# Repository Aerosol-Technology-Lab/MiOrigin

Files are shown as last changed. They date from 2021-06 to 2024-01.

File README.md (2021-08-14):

# MiOrigin
This device is a controller for a bioaerosol collector used by the [Aerosol Technology Lab](https://aerosoltechnologylab.tamu.edu/) of the Biological and Agricultural Engineering Department at Texas A&M University. The MiOrigin controller mimics the MiClone software, which requires a PC connection to use.
 
 ### Features
 - ESP32-WROOM-32E (16MB) MCU
 - 3.5" 480x320 touch-enabled LCD
 - Rechargeable 1000mAh LiPo battery via USB-C connector
 - Built-in male RS-232 port (MAX3232 RS-232 Line Driver) 
 - Over-the-air (OTA) update via BLE

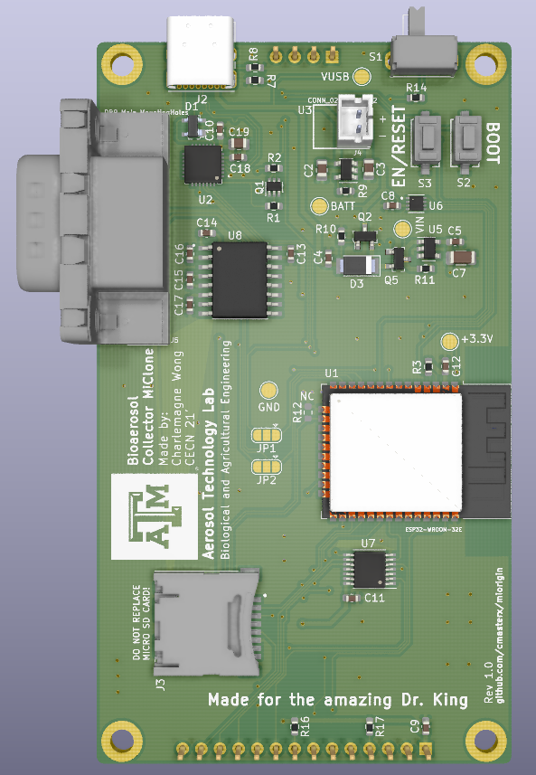
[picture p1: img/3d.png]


## Branches

## USB Drivers for Windows, Linux, macOS
Install CP210x driver if device cannot be detected by computer if connecting to the controller via USB

- Download [CP210x Drivers](https://www.silabs.com/developers/usb-to-uart-bridge-vcp-drivers)

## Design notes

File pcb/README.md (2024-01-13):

# MiOrigin Controller PCB
PCB Schematic and Layour for MiOrigin Controller designed on KiCad

## Revisions
### Rev 1.1 
#### Updates since past revision (Rev 1.0)
1. Moved protection USB diodes to the front of the board
1. Replaced wrong footprint with correct size for the Tri-State Buffer (see Rev 1.0-Known Issue #2)

#### Known Issues
1. RS-232 TX and RX line are switched between the MAX-3232 IC and the D-Sub port. Continuing issue from previous revision (see Rev 1.0-Known Issue #1)

### Rev 1.0
#### Known Issues
1. RS-232 TX and RX line are switched between the MAX-3232 IC and the D-Sub port
1. Footprint for Tri-State Buffer is smaller than actual IC. Careful soldering is required

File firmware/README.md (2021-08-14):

# MiOrigin Controller Firmware
Firmware for MiOrigin Controller

## Setup
1. Install PlatformIO for VS Code
1. Copy boards information from [./boards](boards/) to .platformio boards path

## Build and Flashing Firmware

### Intro
The MiOrigin controller requires two firmwares - a "factory" firmware and an "ota" firmware.

The ota firmware is the actual running firmware during normal operation. This firmware contains the functions that controls the bioaerosol collector. The factory firmware is a special bootloader firmware used to update the ota firmware.

In normal operation, the ota firmware will always boot over the factory firmware. If an update is available over BLE or a new ota firmware is present in the root directory of the MicroSD card, the ota firmware reboots to the factory firmware. The factory firmware flashes the new ota firmware, delete the old copy of the ota firmware in the MicroSD card at `/firmware` (if exists), then places a copy of the new firmware into that directory. If successful, the controller reboots to the newly flashed ota firmware.

### Note

### Flash Factory Firmware
1. Under PlatformIO Extension on the left sidebar, open Project Tasks
1. Select `Build` under `factory` firmware
1. Flash `factory` firwmare with either options:
    1. Connect laptop to control board with a USB-C cable
    1. Select `Upload` to flash directly to firmware
        - Choose this option if this is the first time flashing the board. This will update the correct partition table to the flash
    - add factory firmware with filename `factory.bin` to the root directory of the MicroSD card
        - Note: This is possible only if ota firmware has been previously flashed to the board. This is not possible with a board with no previous programming

### Flash OTA Firmware
1. Under PlatformIO Extension on the left sidebar, open Project Tasks
1. Build `ota` firwmare
1. Flash `factory` firmware with either options 
    - add ota firmware with filename `firmware.bin` to the root directory of the MicroSD card
    1. Connect laptop to control board with a USB-C cable
    1. flash with esptool `$ python3 esptool.py COM_PORT write_flash 0x110000 /path/to/firmware.bin`
        - NOTE: Address used for firmware in flash is `0x110000`. Verify beforing flashing by checking Offset address of `ota_0` in the [partition table](partition_table.csv)

### Pre-compiled firmwares
Pre-compiled firmwares are available at `todo: do this`

## Pipeline
- [x] TFT SPI LCD drivers
- [x] Post scripts that generates pre-compiled firmware/binaries
- [x] WiFi with keep awake
- [x] WiFi WPA
- [ ] WiFi WPA2 Enterprise
- [ ] BLE device settings
- [ ] Update over WiFi

## Known Issues
- Touch screen not working

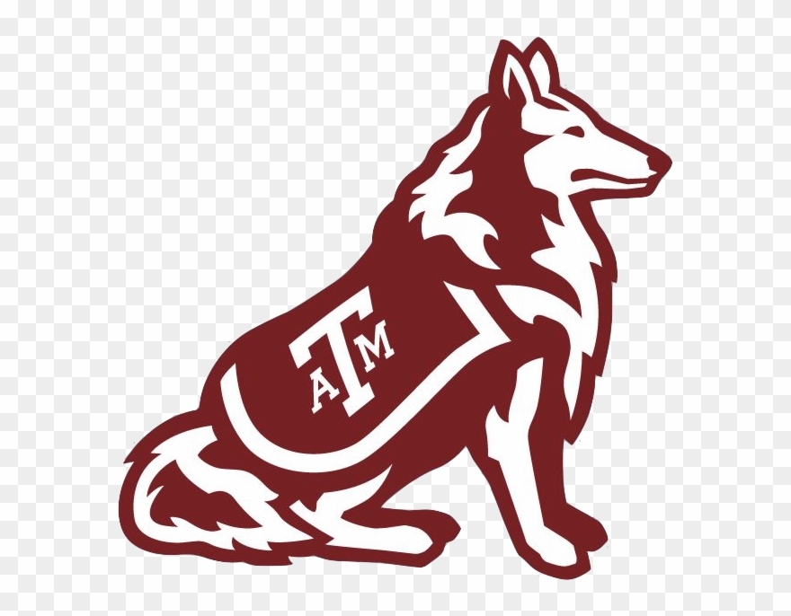
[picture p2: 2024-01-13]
pcb-power-share/power-share/assets/rev.jpg

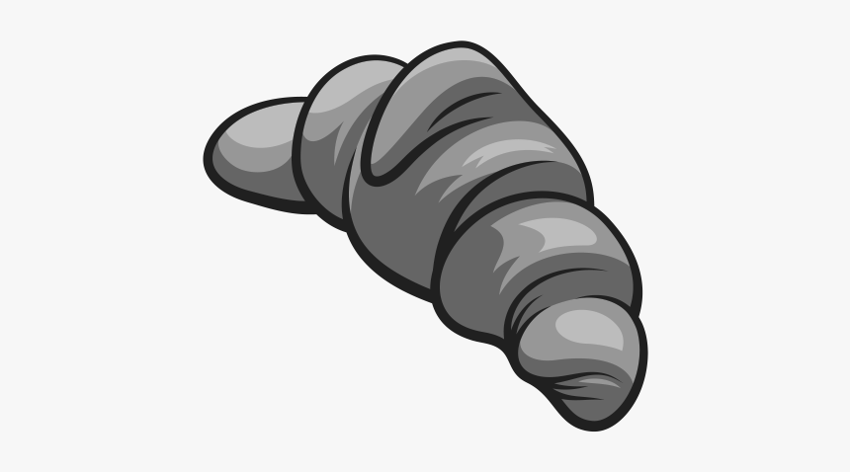
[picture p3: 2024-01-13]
pcb-power-share/power-share/assets/croissant.bmp

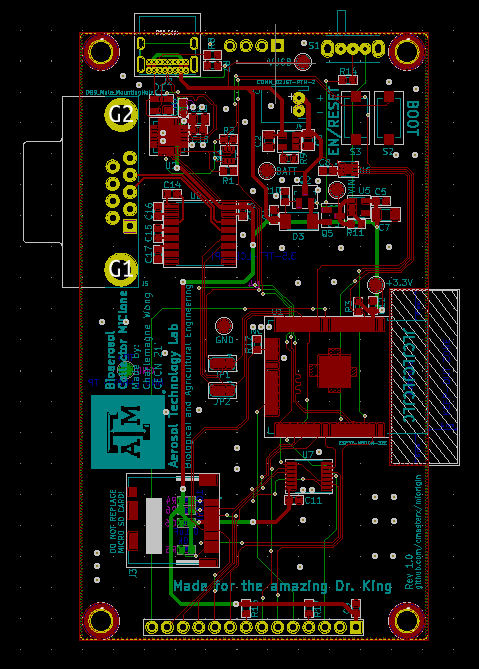
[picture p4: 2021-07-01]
img/outline.png

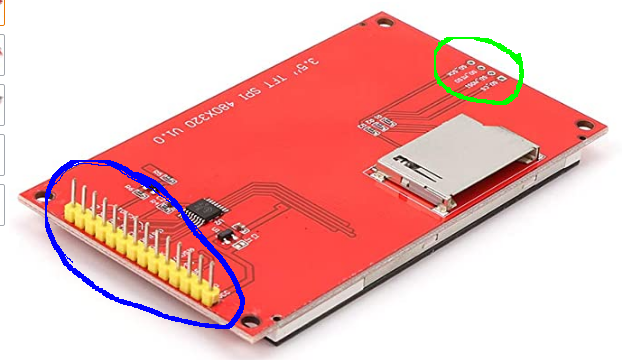
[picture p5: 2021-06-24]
img/display.png

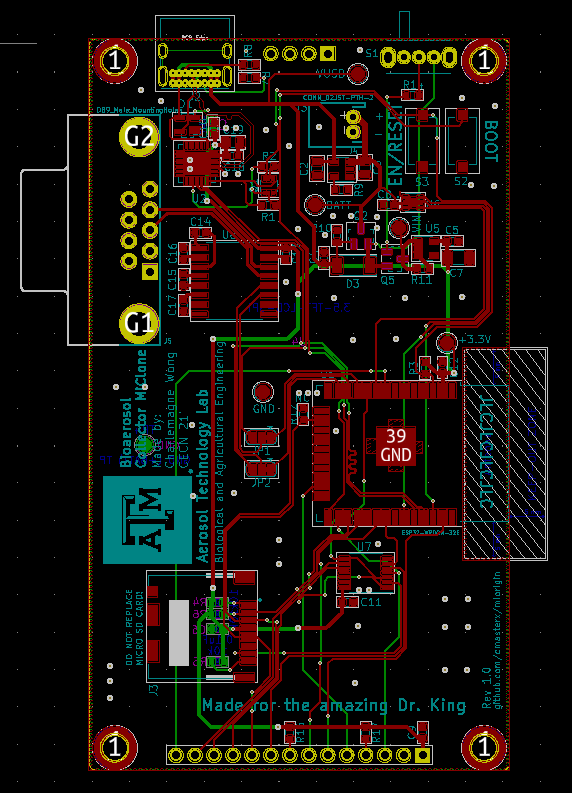
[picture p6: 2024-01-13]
img/outline2.png

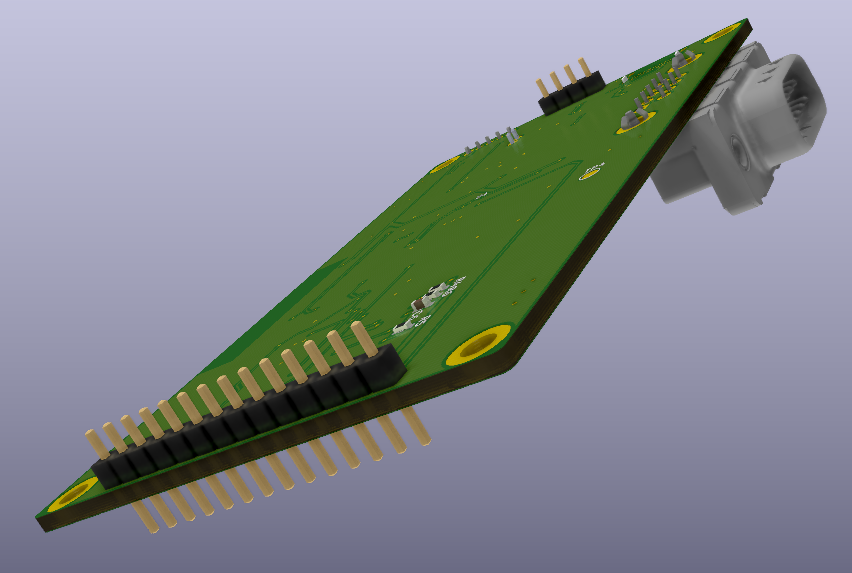
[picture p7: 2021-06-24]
img/Screenshot from 2021-06-24 16-22-36.png

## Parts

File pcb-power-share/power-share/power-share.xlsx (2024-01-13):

Prj: | power-share.xml |  |  |  | Board Qty: | 100
Co.: |  |  |  |  | Unit Cost: | $7.39
Prj date: | Fri 22 Oct 2021 12:46:14 AM CDT |  |  |  | Total Cost: | $738.93 |  |  |  |  | $374.99 | 6 of 15 parts found |  |  |  |  | $839.45 | 8 of 15 parts found |  |  |  |  | $532.62 | 6 of 15 parts found |  |  |  |  | $2.94 | 1 of 15 parts found |  |  |  |  | $483.30 | 7 of 15 parts found |  |  |  |  | $505.60 | 6 of 15 parts found |  |  |  |  | $542.02 | 6 of 15 parts found |  |  |  |  | $41.28 | 1 of 15 parts found
$ date: | 2021-10-22 00:49:18
Global Part Info |  |  |  |  |  |  | Arrow |  |  |  |  |  | Digi-Key |  |  |  |  |  | Farnell |  |  |  |  |  | LCSC |  |  |  |  |  | Mouser |  |  |  |  |  | Newark |  |  |  |  |  | RS Components |  |  |  |  |  | TME
Refs | Value | Footprint | Manf# | Qty | Unit$ | Ext$ | Avail | Purch | Unit$ | MOQ | Ext$ | Cat# | Avail | Purch | Unit$ | MOQ | Ext$ | Cat# | Avail | Purch | Unit$ | MOQ | Ext$ | Cat# | Avail | Purch | Unit$ | MOQ | Ext$ | Cat# | Avail | Purch | Unit$ | MOQ | Ext$ | Cat# | Avail | Purch | Unit$ | MOQ | Ext$ | Cat# | Avail | Purch | Unit$ | MOQ | Ext$ | Cat# | Avail | Purch | Unit$ | MOQ | Ext$ | Cat#
C1 | 22uF | CP_Elec_8x6.5 | 865080643008 | 100 | $0.191 | $19.10 |  |  |  |  |  |  | 8623 |  | $0.198 | 1 | $19.80 | 732-8453-1-ND (https://octopart.com/click/track?ai=8078&sig=08143f3&sid=459&ppid=53914617&vpid=240502649&ct=offers) | NonStk |  | $0.373 | 1 | $37.28 | 2466335 (https://octopart.com/click/track?c=1&ai=8078&sig=09a3c48&sid=819&ppid=53914617&vpid=209558840&ct=offers) |  |  |  |  |  |  | NonStk |  | $0.191 | 1 | $19.10 | 710865080643008 (https://octopart.com/click/track?c=1&ai=8078&sig=0967f77&sid=2401&ppid=53914617&vpid=416614858&ct=offers) | NonStk |  | $0.253 | 1 | $25.30 | 40Y4050 (https://octopart.com/click/track?c=1&ai=8078&sig=09bb828&sid=2402&ppid=53914617&vpid=184773775&ct=offers) | 225 |  | $0.287 | 25 | $28.72 | 8391874 (https://octopart.com/click/track?ai=8078&sig=06ba437&sid=10022&ppid=53914617&vpid=199199319&ct=offers)
C2 | 6.8uF | C_1812_4532Metric | C4532X7R1H685K250KB | 100 | $0.768 | $76.85 | NonStk |  | $1.207 | 1 | $120.71 | C4532X7R1H685K250KB (https://octopart.com/click/track?c=1&ai=8078&sig=0d2d5fb&sid=1106&ppid=25947926&vpid=486097657&ct=offers) | 19867 |  | $0.768 | 1 | $76.85 | 445-3919-1-ND (https://octopart.com/click/track?ai=8078&sig=02ae9c6&sid=459&ppid=25947926&vpid=63975951&ct=offers) | 59500 |  | $0.850 | 1 | $85.04 | 1843170 (https://octopart.com/click/track?ai=8078&sig=0c89169&sid=819&ppid=25947926&vpid=139697936&ct=offers) |  |  |  |  |  |  | 8166 |  | $0.769 | 1 | $76.90 | 810C4532X7R1H685K (https://octopart.com/click/track?ai=8078&sig=00ac762&sid=2401&ppid=25947926&vpid=66164902&ct=offers) | 59000 |  | $1.060 | 1 | $106.00 | 13T1119 (https://octopart.com/click/track?ai=8078&sig=08b8ed0&sid=2402&ppid=25947926&vpid=260822761&ct=offers) | 16131 |  | $1.483 | 5 | $148.28 | 7416825 (https://octopart.com/click/track?ai=8078&sig=0acb252&sid=10022&ppid=25947926&vpid=199138110&ct=offers)
C3 | 10nF | C_0402_1005Metric_Pad0.74x0.62mm_HandSolder | GCM155R71H103KA55D | 100 | $0.013 | $1.29 | 2269 |  |  | 10000 |  | GCM155R71H103KA55D (https://octopart.com/click/track?ai=8078&sig=0baf4ca&sid=1106&ppid=9105516&vpid=473329314&ct=offers) | 25744106 |  | $0.013 | 1 | $1.29 | 490-4762-1-ND (https://octopart.com/click/track?ai=8078&sig=05479c9&sid=459&ppid=9105516&vpid=34232110&ct=offers) | 8250000 |  | $0.021 | 10 | $2.06 | 2470416RL (https://octopart.com/click/track?ai=8078&sig=0119398&sid=819&ppid=9105516&vpid=220678719&ct=offers) | 97850 |  | $0.029 | 50 | $2.94 | C91601 (https://octopart.com/click/track?ai=8078&sig=0ec5f8f&sid=27971&ppid=9105516&vpid=445986708&ct=offers) | 7456658 |  | $0.018 | 1 | $1.80 | 81GCM155R71H103KA5D (https://octopart.com/click/track?ai=8078&sig=048b060&sid=2401&ppid=9105516&vpid=37821366&ct=offers) | 8250000 |  | $0.022 | 1 | $2.20 | 45Y5159 (https://octopart.com/click/track?ai=8078&sig=031832d&sid=2402&ppid=9105516&vpid=231884079&ct=offers) | 607000 |  |  | 200 |  | 7234954 (https://octopart.com/click/track?ai=8078&sig=0a8e140&sid=10022&ppid=9105516&vpid=199071532&ct=offers)
C4 | 120uF | C_Elec_4x5.8 | https://b2b-api.panasonic.eu/file_stream/pids/fileversion/9127 | 100
C5,C7 | 10uF | C_0805_2012Metric | CL21B106KOQNNNG | 200 | $0.101 | $20.22 | NonStk |  |  |  |  | CL21B106KOQNNNG (https://octopart.com/click/track?c=1&ai=8078&sig=0d92234&sid=1106&ppid=19995691&vpid=486018040&ct=offers) | 48876 |  | $0.101 | 1 | $20.22 | 1276-6472-1-ND (https://octopart.com/click/track?ai=8078&sig=0afb040&sid=459&ppid=19995691&vpid=254014560&ct=offers) |  |  |  |  |  |  |  |  |  |  |  |  | NonStk |  | $0.108 | 1 | $21.60 | 187CL21B106KOQNNNG (https://octopart.com/click/track?c=1&ai=8078&sig=0bf9aa6&sid=2401&ppid=19995691&vpid=659501626&ct=offers)
C6,C8 | 0.1uF | C_0603_1608Metric |  | 200
D1,D2 | PMEG6030EP | D_SOD-128 | PMEG6030ETPX (https://assets.nexperia.com/documents/data-sheet/PMEG6030EP.pdf) | 200 | $0.206 | $41.28 | 3000 |  |  | 3000 |  | PMEG6030ETPX (https://octopart.com/click/track?ai=8078&sig=0b6b405&sid=1106&ppid=78741541&vpid=484943718&ct=offers) | 67725 |  | $0.312 | 1 | $62.46 | 1727-1348-1-ND (https://octopart.com/click/track?ai=8078&sig=040e61e&sid=459&ppid=78741541&vpid=417206306&ct=offers) | 6668 |  | $0.422 | 5 | $84.49 | 2311228 (https://octopart.com/click/track?ai=8078&sig=05bc89f&sid=11744&ppid=78741541&vpid=511495904&ct=offers) |  |  |  |  |  |  | 12235 |  | $0.313 | 1 | $62.60 | 771PMEG6030ETPX (https://octopart.com/click/track?ai=8078&sig=0efc8e0&sid=2401&ppid=78741541&vpid=416182149&ct=offers) | 6668 |  | $0.410 | 1 | $82.00 | 84W8061 (https://octopart.com/click/track?ai=8078&sig=0a6d674&sid=2402&ppid=78741541&vpid=511736070&ct=offers) | 17025 |  | $0.418 | 25 | $83.66 | 1513110 (https://octopart.com/click/track?ai=8078&sig=0a62c34&sid=10022&ppid=78741541&vpid=501184399&ct=offers) | NonStk |  | $0.206 | 3 | $41.28 | PMEG6030ETPX (https://octopart.com/click/track?ai=8078&sig=0e56a21&sid=1532&ppid=78741541&vpid=709102829&ct=offers)
J1 | CONN_02JST-PTH-2 | JST-2-PTH |  | 100
L1 | 12uH | L_Bourns_SRR1260 | SRR1260-120M | 100 | $0.761 | $76.10 | 106800 |  | $1.177 | 1 | $117.70 | SRR1260120M (https://octopart.com/click/track?ai=8078&sig=03edc0d&sid=1106&ppid=1809450&vpid=485293645&ct=offers) | 8881 |  | $0.912 | 1 | $91.22 | SRR1260-120MCT-ND (https://octopart.com/click/track?ai=8078&sig=090dfbb&sid=459&ppid=1809450&vpid=34264395&ct=offers) | 703 |  | $1.029 | 1 | $102.85 | 2859155 (https://octopart.com/click/track?ai=8078&sig=05832f3&sid=819&ppid=1809450&vpid=489898128&ct=offers) |  |  |  |  |  |  | 284 |  | $0.913 | 1 | $91.30 | 652SRR1260120M (https://octopart.com/click/track?ai=8078&sig=0148666&sid=2401&ppid=1809450&vpid=37689357&ct=offers) | 600 |  | $0.761 | 1 | $76.10 | 02J3129 (https://octopart.com/click/track?ai=8078&sig=082c0d0&sid=2402&ppid=1809450&vpid=30080066&ct=offers) | 410 |  |  | 600 |  | 1728556 (https://octopart.com/click/track?ai=8078&sig=066dc14&sid=10022&ppid=1809450&vpid=501025689&ct=offers)
P1,P2 | Molex-KK-396-5POS | Molex-KK-396-5POS | 0026614050 (http://datasheet.octopart.com/26-61-4050-Molex-datasheet-10742124.pdf) | 200 | $0.683 | $136.58 | 10 |  | $0.683 | 1 | $136.58 | 26614050 (https://octopart.com/click/track?ai=8078&sig=0e9ed3d&sid=1106&ppid=277946&vpid=485824018&ct=offers) | 4094 |  | $1.000 | 1 | $200.10 | WM5227-ND (https://octopart.com/click/track?ai=8078&sig=00f8485&sid=459&ppid=277946&vpid=83331319&ct=offers) | 1917 |  | $1.104 | 1 | $220.89 | 2888936 (https://octopart.com/click/track?ai=8078&sig=072aa6b&sid=11744&ppid=277946&vpid=494603043&ct=offers) |  |  |  |  |  |  | 2082 |  | $1.050 | 1 | $210.00 | 53826614050 (https://octopart.com/click/track?ai=8078&sig=0c7f5bf&sid=2401&ppid=277946&vpid=37607263&ct=offers) | 109 |  | $1.070 | 1 | $214.00 | 71H2284 (https://octopart.com/click/track?ai=8078&sig=003de6d&sid=2402&ppid=277946&vpid=3022709&ct=offers) | 262 |  | $1.407 | 10 | $281.36 | 6703083 (https://octopart.com/click/track?ai=8078&sig=0c54271&sid=10022&ppid=277946&vpid=199067350&ct=offers)
R1 | 470k | R_0603_1608Metric |  | 100
R2 | 200k | R_0603_1608Metric |  | 100
R3 | 2.0k | R_0603_1608Metric |  | 100
R4 | 1.0k | R_0603_1608Metric |  | 100
U1 | LM22680 | LM22680 | LM22680QMRX-ADJ/NOPB (https://octopart.com/click/track?ai=8078&ct=datasheets&sig=0f7457e&at=physicalpart&sid=370&ppid=24844189&hlid=29970811) | 100 | $3.675 | $367.51 | NonStk |  |  | 2500 |  | LM22680QMRXADJ/NOPB (https://octopart.com/click/track?c=1&ai=8078&sig=0cd224b&sid=1106&ppid=24844189&vpid=631806381&ct=offers) | 487 |  | $3.675 | 1 | $367.51 | 296-45541-1-ND (https://octopart.com/click/track?c=1&ai=8078&sig=0084cb7&sid=459&ppid=24844189&vpid=419012817&ct=offers)
 | Used currency rates: |  |  |  | Total Purchase: | $0.00 | Buy here (https://www.arrow.com/en/bom-tool/) |  |  |  | $0.00 |  | Buy here (https://www.digikey.com/ordering/shoppingcart) |  |  |  | $0.00 |  | Buy here (https://fr.farnell.com/en-FR/quick-order?isQuickPaste=true) |  |  |  | $0.00 |  | Buy here (https://lcsc.com/bom.html) |  |  |  | $0.00 |  | Buy here (https://mouser.com/bom/) |  |  |  | $0.00 |  | Buy here (https://www.newark.com/quick-order?isQuickPaste=true) |  |  |  | $0.00 |  | Buy here (https://uk.rs-online.com/web/mylists/manualQuotes.html?method=showEnquiryCreationPage&mode=new) |  |  |  | $0.00 |  | Buy here (https://www.tme.eu/en/Profile/QuickBuy/load.html) |  |  |  | $0.00
 | USD($)/GBP(£): | 1.380590817 |  |  | Purchase description: |  |  |  |  |  |  |  |  |  |  |  |  |  |  |  |  |  |  |  |  | Copy this header and order to a CSV file and use it for JLCPCB manufacturer PCB house. The multipart components that use "#" symbol are not allowed by JLCPCB.
KiCost® v1.1.6

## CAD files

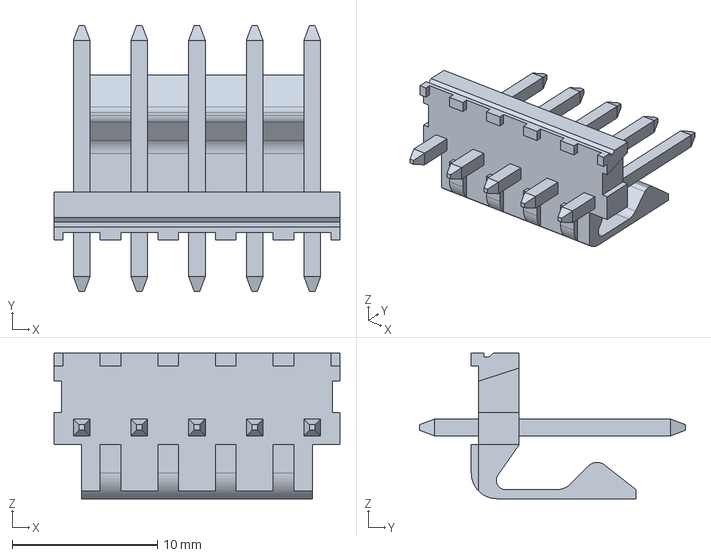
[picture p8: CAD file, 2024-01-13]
pcb-power-share/power-share/cad-models/kk396-5pos.stp
19.7 x 18.3 x 10.0 mm

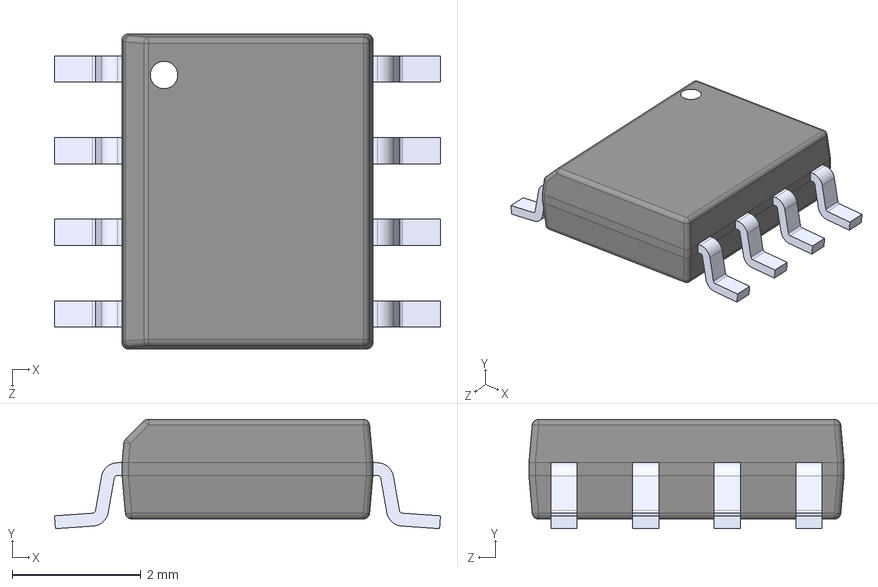
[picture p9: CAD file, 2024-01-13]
pcb-power-share/power-share/cad-models/LM22680.step
6.00 x 1.70 x 4.90 mm

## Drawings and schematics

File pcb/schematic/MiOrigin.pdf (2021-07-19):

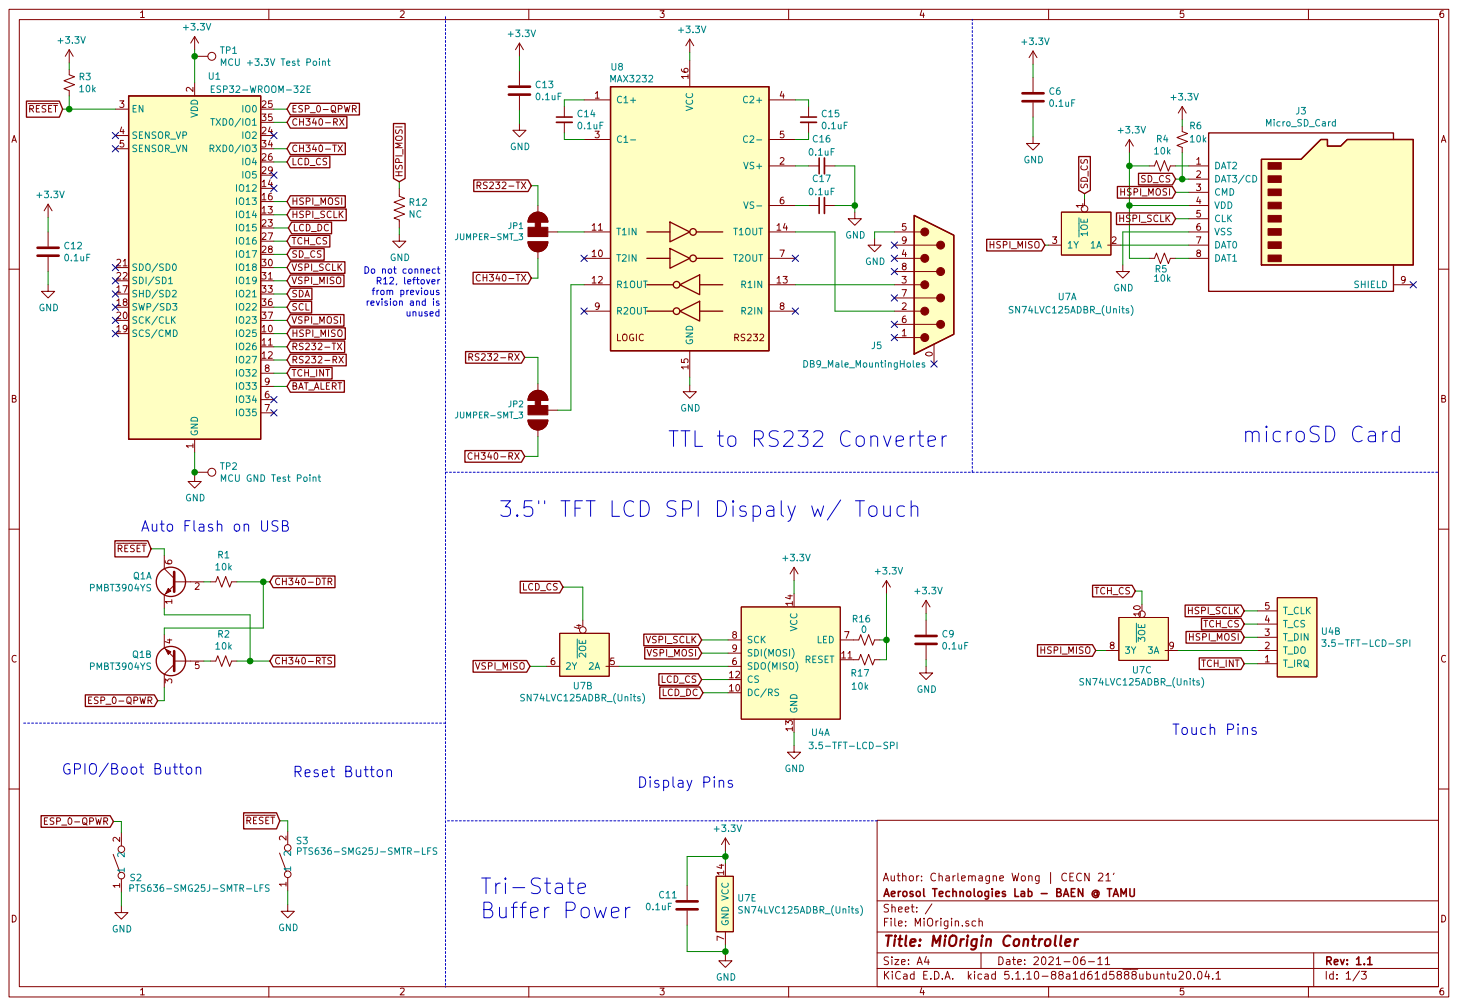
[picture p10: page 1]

TP1MCU +3.3V Test Point TP2 MCU GND Test Point R2

2 SCK/CLK 20 SDO/SD0 21 SDI/SD1 22

Do not connect R12, leftover

3.5" TFT LCD SPI Dispaly w/ Touch

Auto Flash on USB

3.5-TFT-LCD-SPI GND

Author: Charlemagne Wong | CECN 21'
File: MiOrigin.sch Sheet: / Aerosol Technologies Lab - BAEN @ TAMU

Id: 1/3 Title: MiOrigin Controller

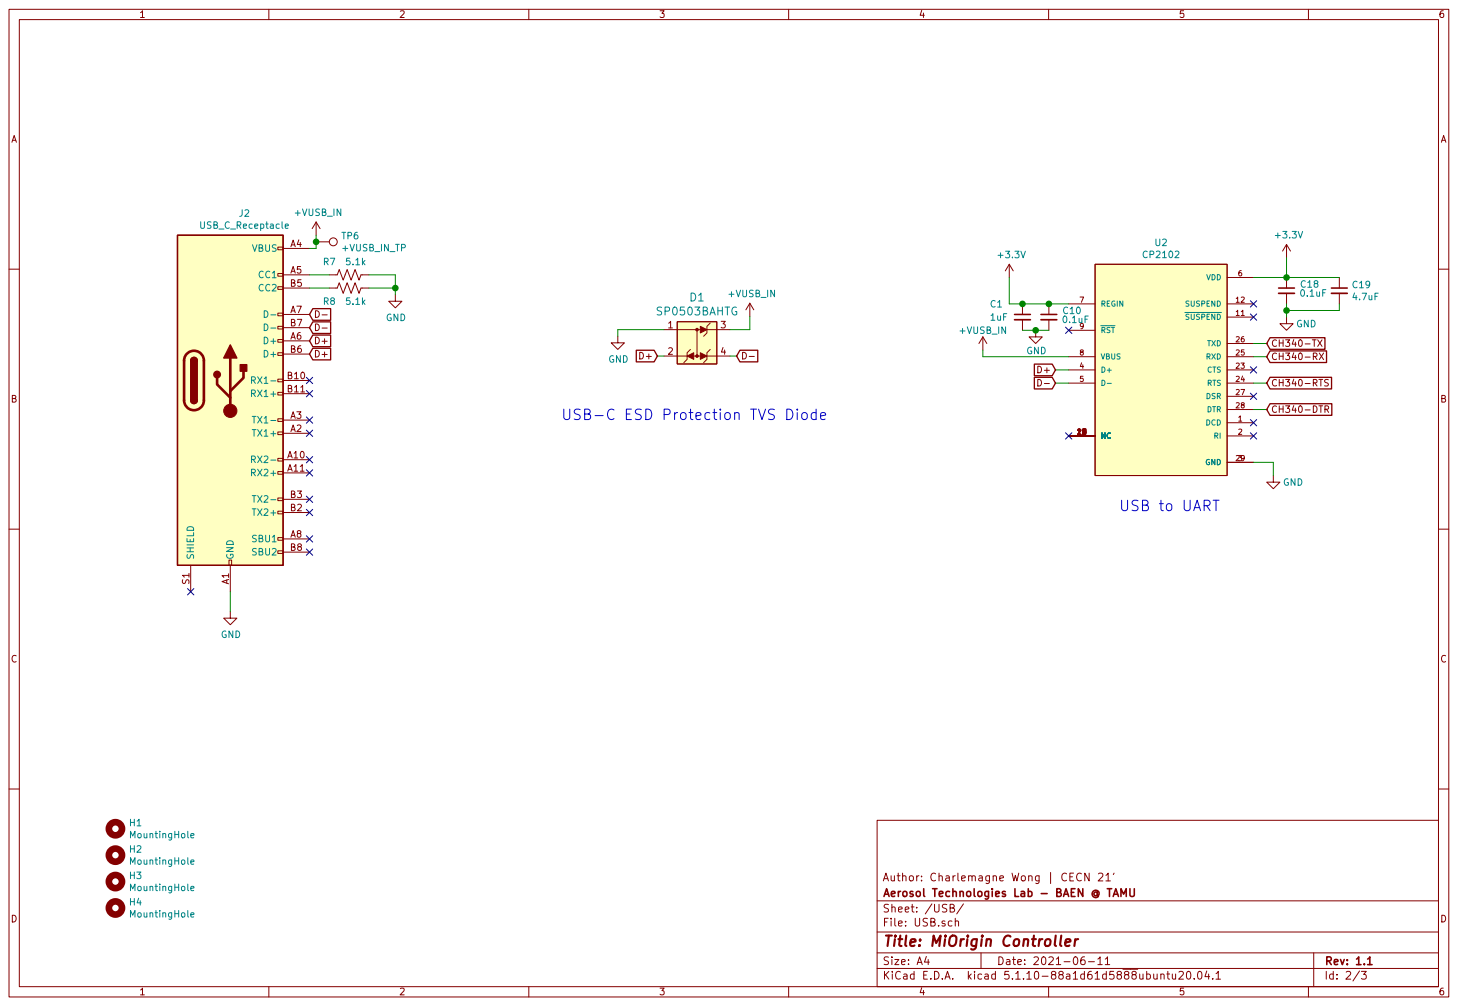
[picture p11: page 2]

USB-C ESD Protection TVS Diode

Author: Charlemagne Wong | CECN 21'
Id: 2/3 Title: MiOrigin Controller File: USB.sch Sheet: /USB/ Aerosol Technologies Lab - BAEN @ TAMU

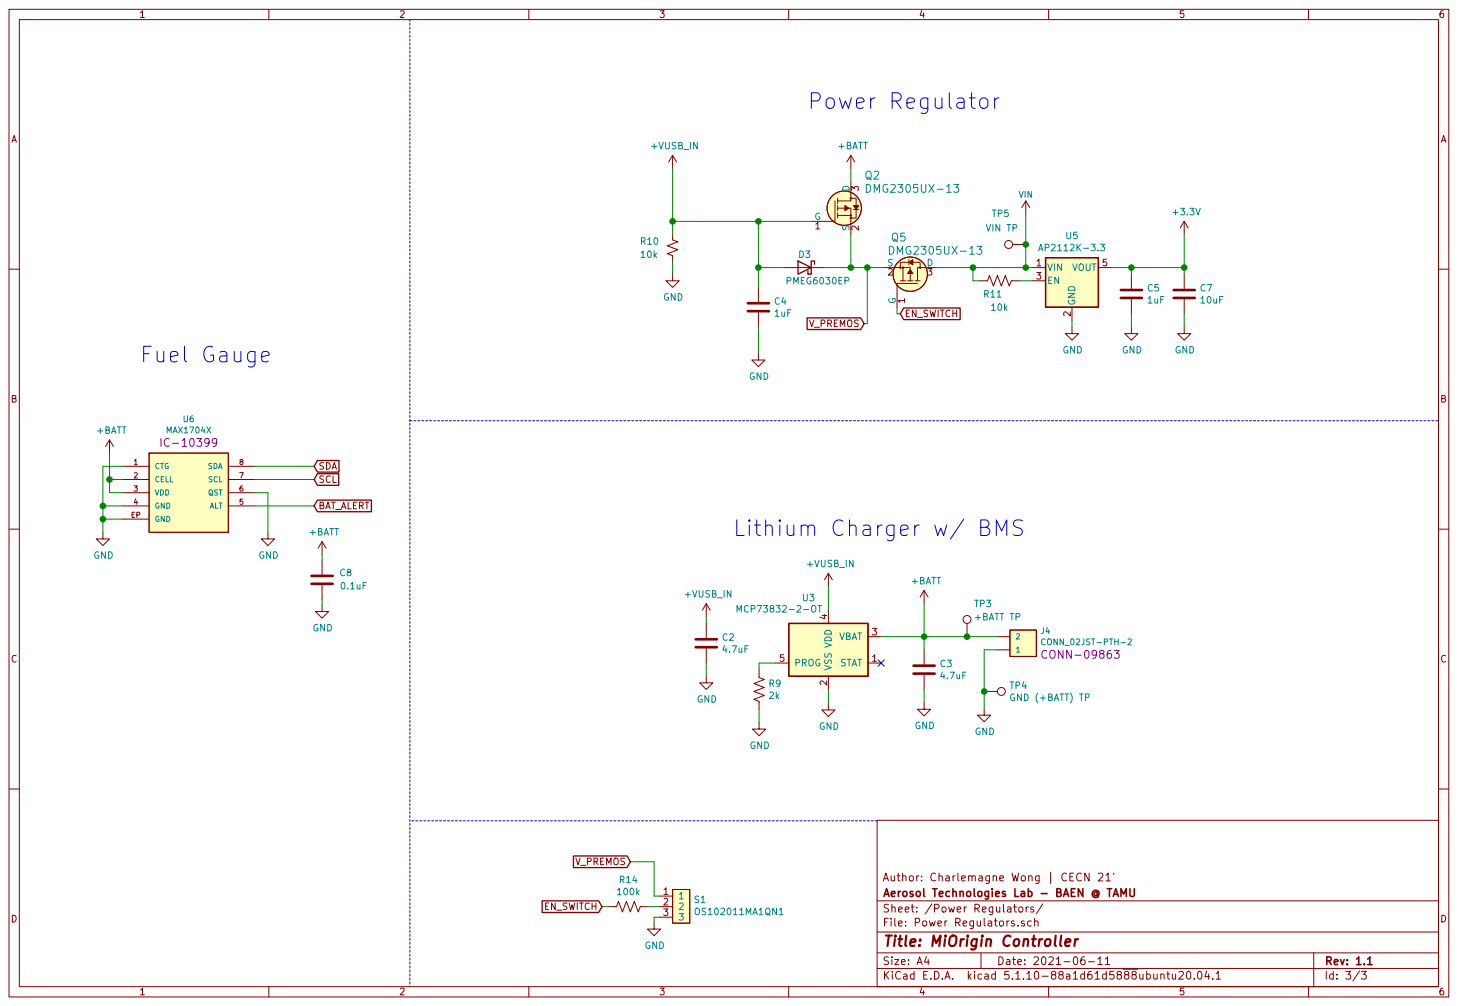
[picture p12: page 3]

Author: Charlemagne Wong | CECN 21' C3

Aerosol Technologies Lab - BAEN @ TAMU
Sheet: /Power Regulators/
File: Power Regulators.sch
Id: 3/3 Title: MiOrigin Controller

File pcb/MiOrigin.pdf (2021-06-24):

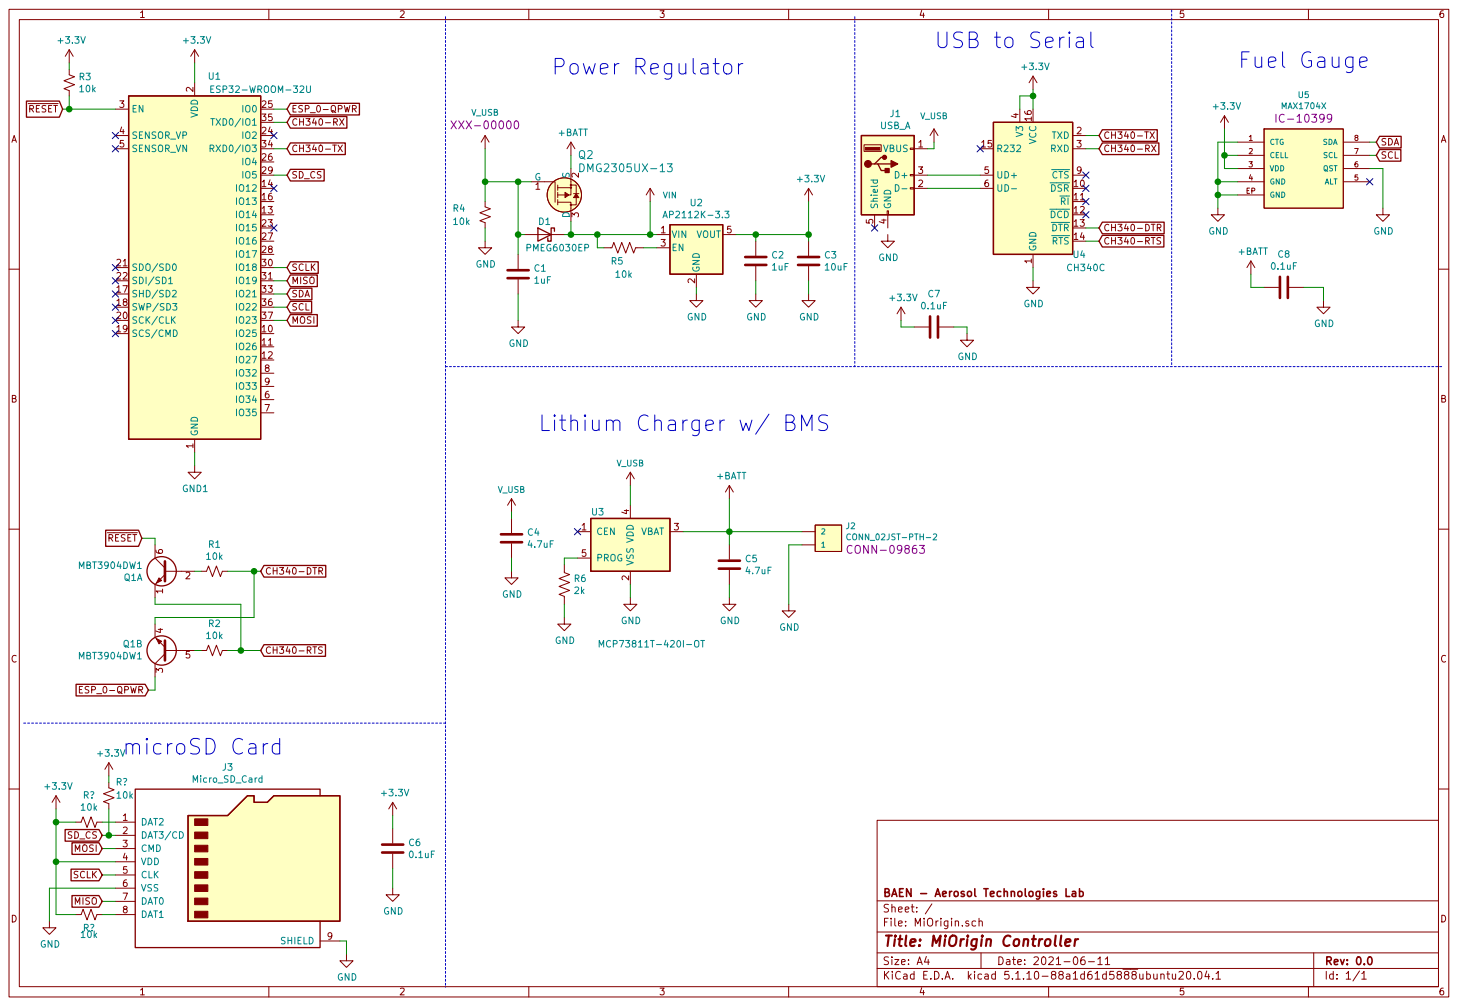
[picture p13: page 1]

2 SCK/CLK 20 SDO/SD0 21 SDI/SD1 22

1 DSR 10 RI 11 DCD 12 DTR 13 RTS 14 R232 15 VCC 16 TXD 2 RXD 3 V3

4 PROG 5 U3 MCP73811T-420I-OT GND GND

File: MiOrigin.sch Sheet: / BAEN - Aerosol Technologies Lab

Id: 1/1 Title: MiOrigin Controller

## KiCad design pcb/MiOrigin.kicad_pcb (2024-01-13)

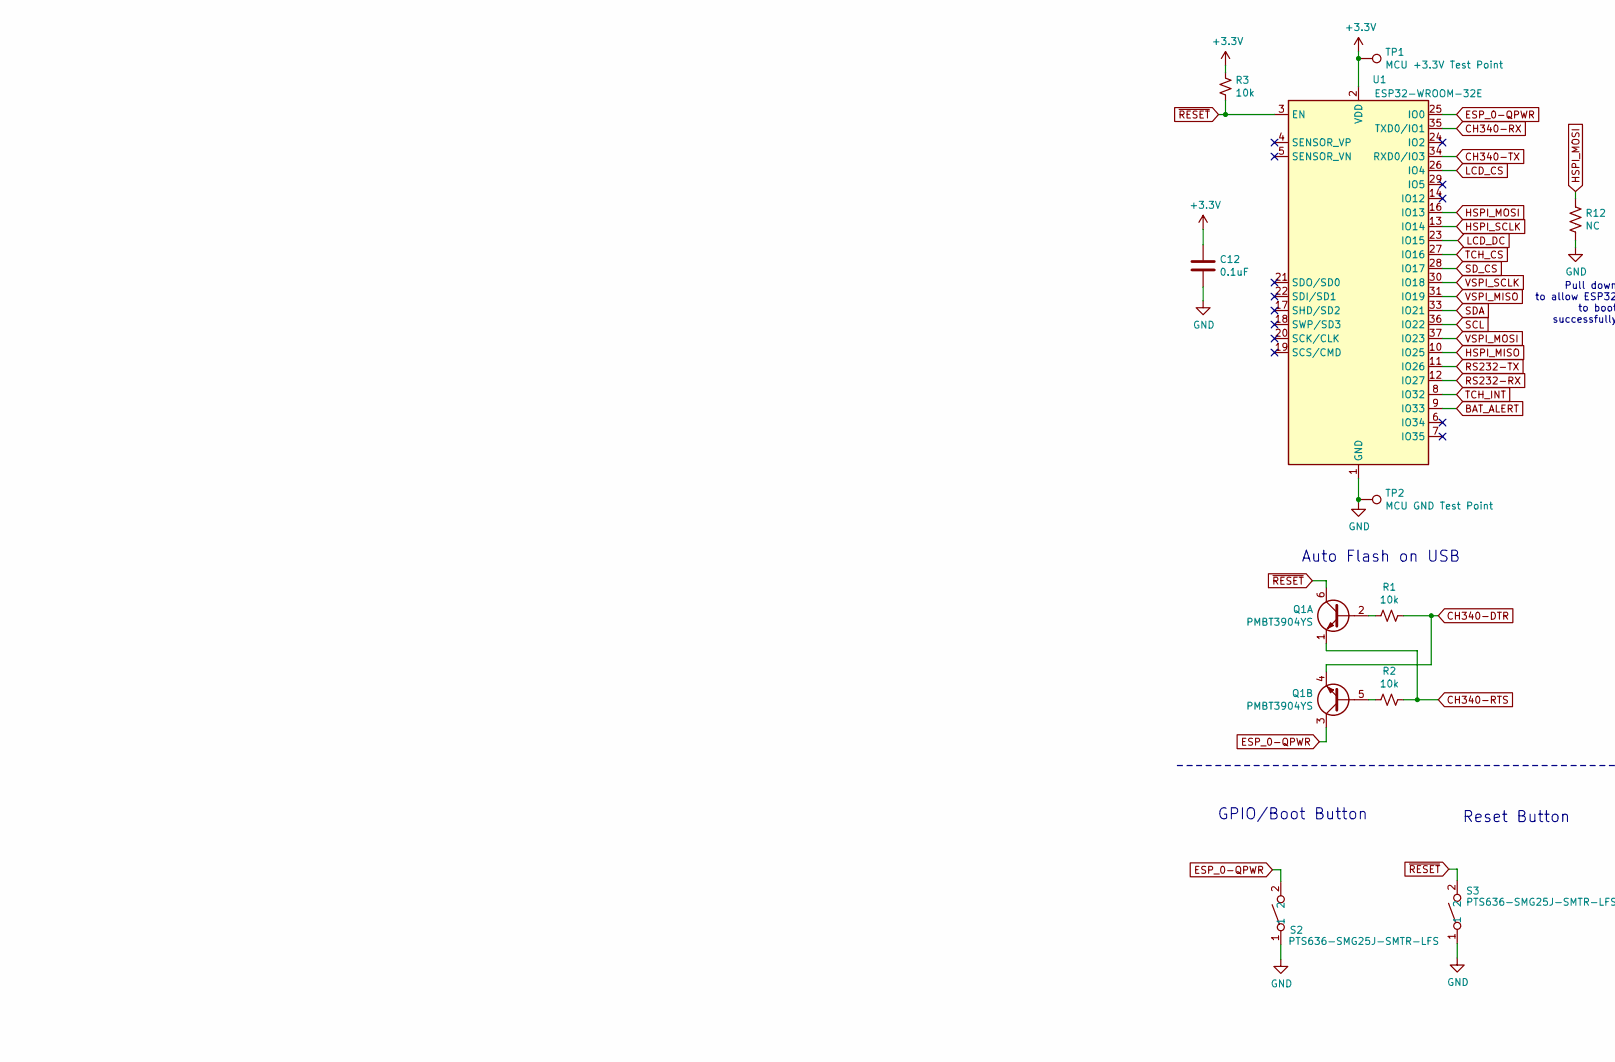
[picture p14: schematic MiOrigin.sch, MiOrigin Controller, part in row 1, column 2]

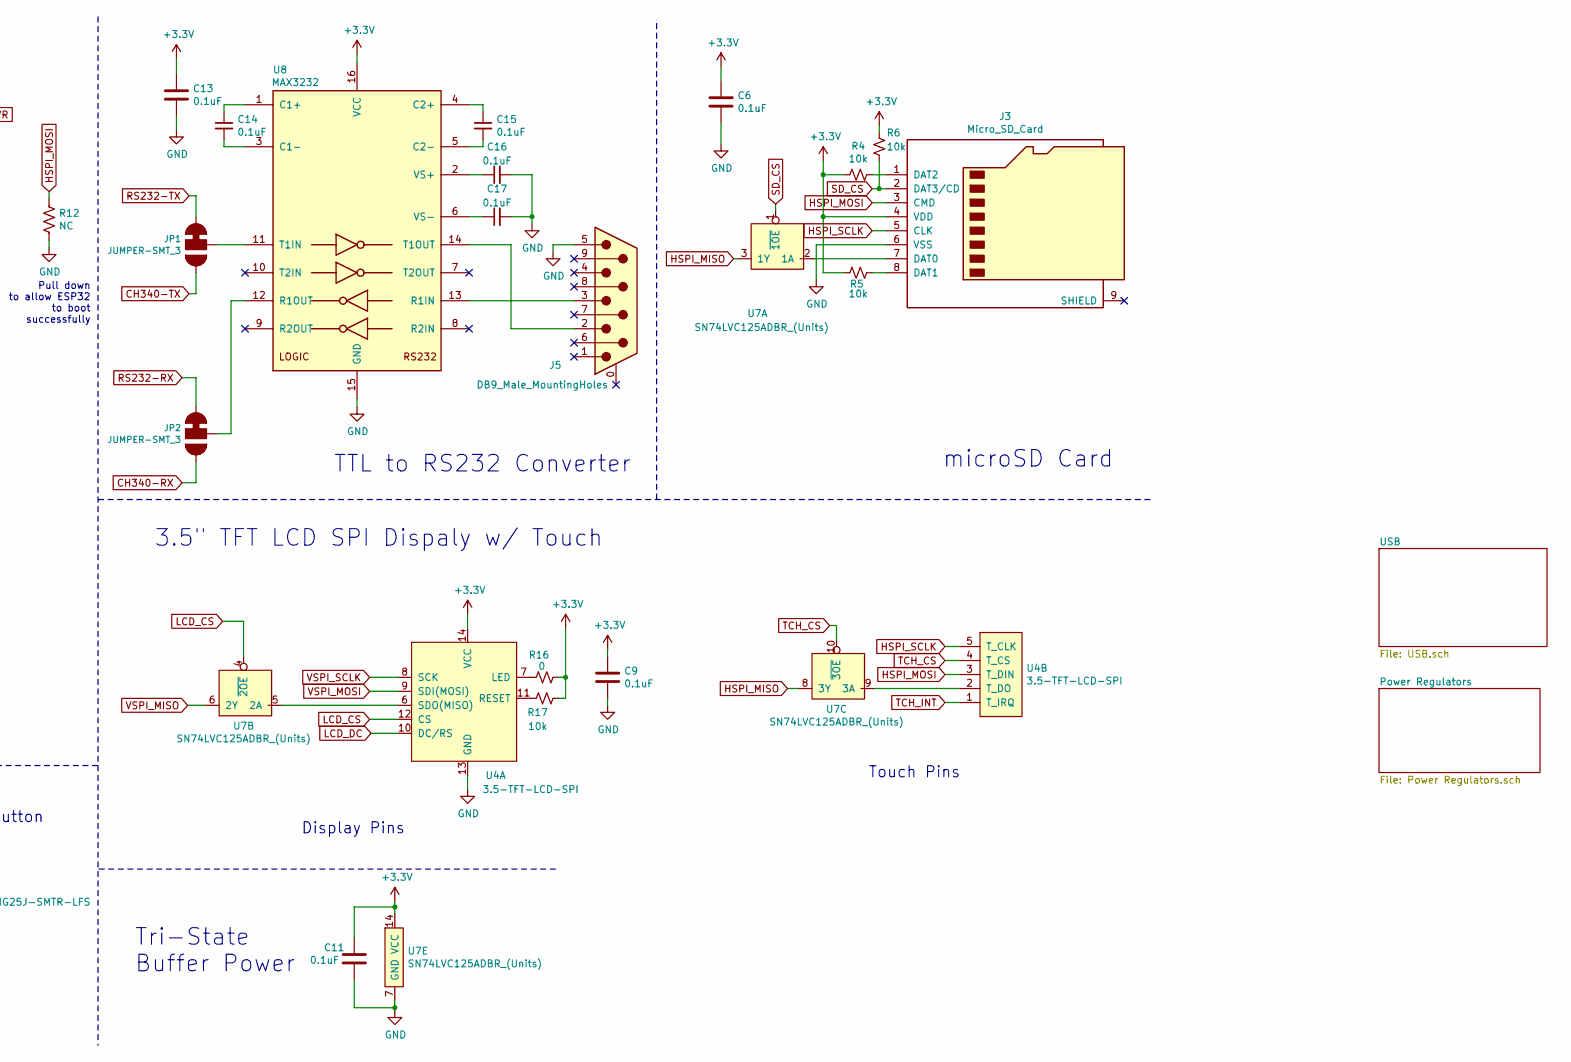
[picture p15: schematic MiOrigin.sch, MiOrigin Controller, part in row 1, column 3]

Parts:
C6, C9, C11, C12, C13, C14, C15, C16, C17: 0.1uF; C_0603_1608Metric
J3: Micro_SD_Card; HRS_DM3CS-SF
J5: DB9_Male_MountingHoles; DB9_MALE; MPN LD09P33E4GX00LF
JP1, JP2: JUMPER-SMT_3; SolderJumper-3_P1.3mm_Bridged12_RoundedPad1.0x1.5mm
Q1: PMBT3904YS; SOT-363_SC-70-6
R1, R2, R3, R4, R5, R6, R17: 10k; R_0603_1608Metric
R12: NC; R_0603_1608Metric
R16: 0; R_0603_1608Metric
S2, S3: PTS636-SMG25J-SMTR-LFS; PTS636SK50SMTRLFS
TP1: MCU +3.3V Test Point; TestPoint_Pad_D2.0mm
TP2: MCU GND Test Point; TestPoint_Pad_D2.0mm
U1: ESP32-WROOM-32E; ESP32-WROOM-32; MPN ESP32-WROOM-32E (4MB HIGH TEMP)
U4: 3.5-TFT-LCD-SPI
U7: SN74LVC125ADBR_(Units); TSSOP-14_4.4x5mm_P0.65mm
U8: MAX3232; SOIC127P1030X265-16N; MPN MAX3232EIDWR

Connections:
+3V3: C6.1, C9.1, C11.1, C12.1, C13.1, J3.4 (VDD), R3.1, R4.2, R5.2, R6.2, R16.1, R17.1, TP1.1, U1.2 (VDD), U4.14 (VCC), U7.14 (VCC), U8.16 (VCC); also elsewhere on the board
BAT_ALERT: U1.9 (IO33); also elsewhere on the board
CH340-DTR: Q1.4 (E2), R1.1; also elsewhere on the board
CH340-RTS: Q1.1 (E1), R2.1; also elsewhere on the board
CH340-RX: JP2.3, U1.35 (TXD0/IO1); also elsewhere on the board
CH340-TX: JP1.3, U1.34 (RXD0/IO3); also elsewhere on the board
ESP_0-QPWR: Q1.3 (C2), S2.2, U1.25 (IO0)
GND: C6.2, C9.2, C11.2, C12.2, C13.2, C16.2, C17.2, J3.6 (VSS), J5.5, R12.2, S2.1, S3.1, TP2.1, U1.1 (GND), U1.15 (GND), U1.38 (GND), U1.39 (GND), U4.13 (GND), U7.7 (GND), U8.15 (GND); also elsewhere on the board
HSPI_MISO: U1.10 (IO25), U7.3 (1Y), U7.8 (3Y)
HSPI_MOSI: J3.3 (CMD), R12.1, U1.16 (IO13), U4.3 (T_DIN)
HSPI_SCLK: J3.5 (CLK), U1.13 (IO14), U4.5 (T_CLK)
LCD_CS: U1.26 (IO4), U4.12 (CS), U7.4 (~2OE)
LCD_DC: U1.23 (IO15), U4.10 (DC/RS)
unnamed: C14.1, U8.1 (C1+)
unnamed: C14.2, U8.3 (C1-)
unnamed: C15.1, U8.4 (C2+)
unnamed: C15.2, U8.5 (C2-)
unnamed: C16.1, U8.2 (VS+)
unnamed: C17.1, U8.6 (VS-)
unnamed: J3.1 (DAT2), R4.1
unnamed: J3.7 (DAT0), U7.2 (1A)
unnamed: J3.8 (DAT1), R5.1
unnamed: J5.2, U8.14 (T1OUT)
unnamed: J5.3, U8.13 (R1IN)
unnamed: JP1.2, U8.11 (T1IN)
unnamed: JP2.2, U8.12 (R1OUT)
unnamed: Q1.2 (B1), R1.2
unnamed: Q1.5 (B2), R2.2
unnamed: R16.2, U4.7 (LED)
unnamed: R17.2, U4.11 (RESET)
unnamed: U4.2 (T_DO), U7.9 (3A)
unnamed: U4.6 (SDO(MISO)), U7.5 (2A)
RS232-RX: JP2.1, U1.12 (IO27)
RS232-TX: JP1.1, U1.11 (IO26)
SCL: U1.36 (IO22); also elsewhere on the board
SDA: U1.33 (IO21); also elsewhere on the board
SD_CS: J3.2 (DAT3/CD), R6.1, U1.28 (IO17), U7.1 (~1OE)
TCH_CS: U1.27 (IO16), U4.4 (T_CS), U7.10 (~3OE)
TCH_INT: U1.8 (IO32), U4.1 (T_IRQ)
VSPI_MISO: U1.31 (IO19), U7.6 (2Y)
VSPI_MOSI: U1.37 (IO23), U4.9 (SDI(MOSI))
VSPI_SCLK: U1.30 (IO18), U4.8 (SCK)
~RESET: Q1.6 (C1), R3.2, S3.2, U1.3 (EN)

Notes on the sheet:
microSD Card
Pull down to allow ESP32 to boot successfully
GPIO/Boot Button
Reset Button
Tri-State Buffer Power
Auto Flash on USB
TTL to RS232 Converter
3.5" TFT LCD SPI Dispaly w/ Touch
Touch Pins
Display Pins

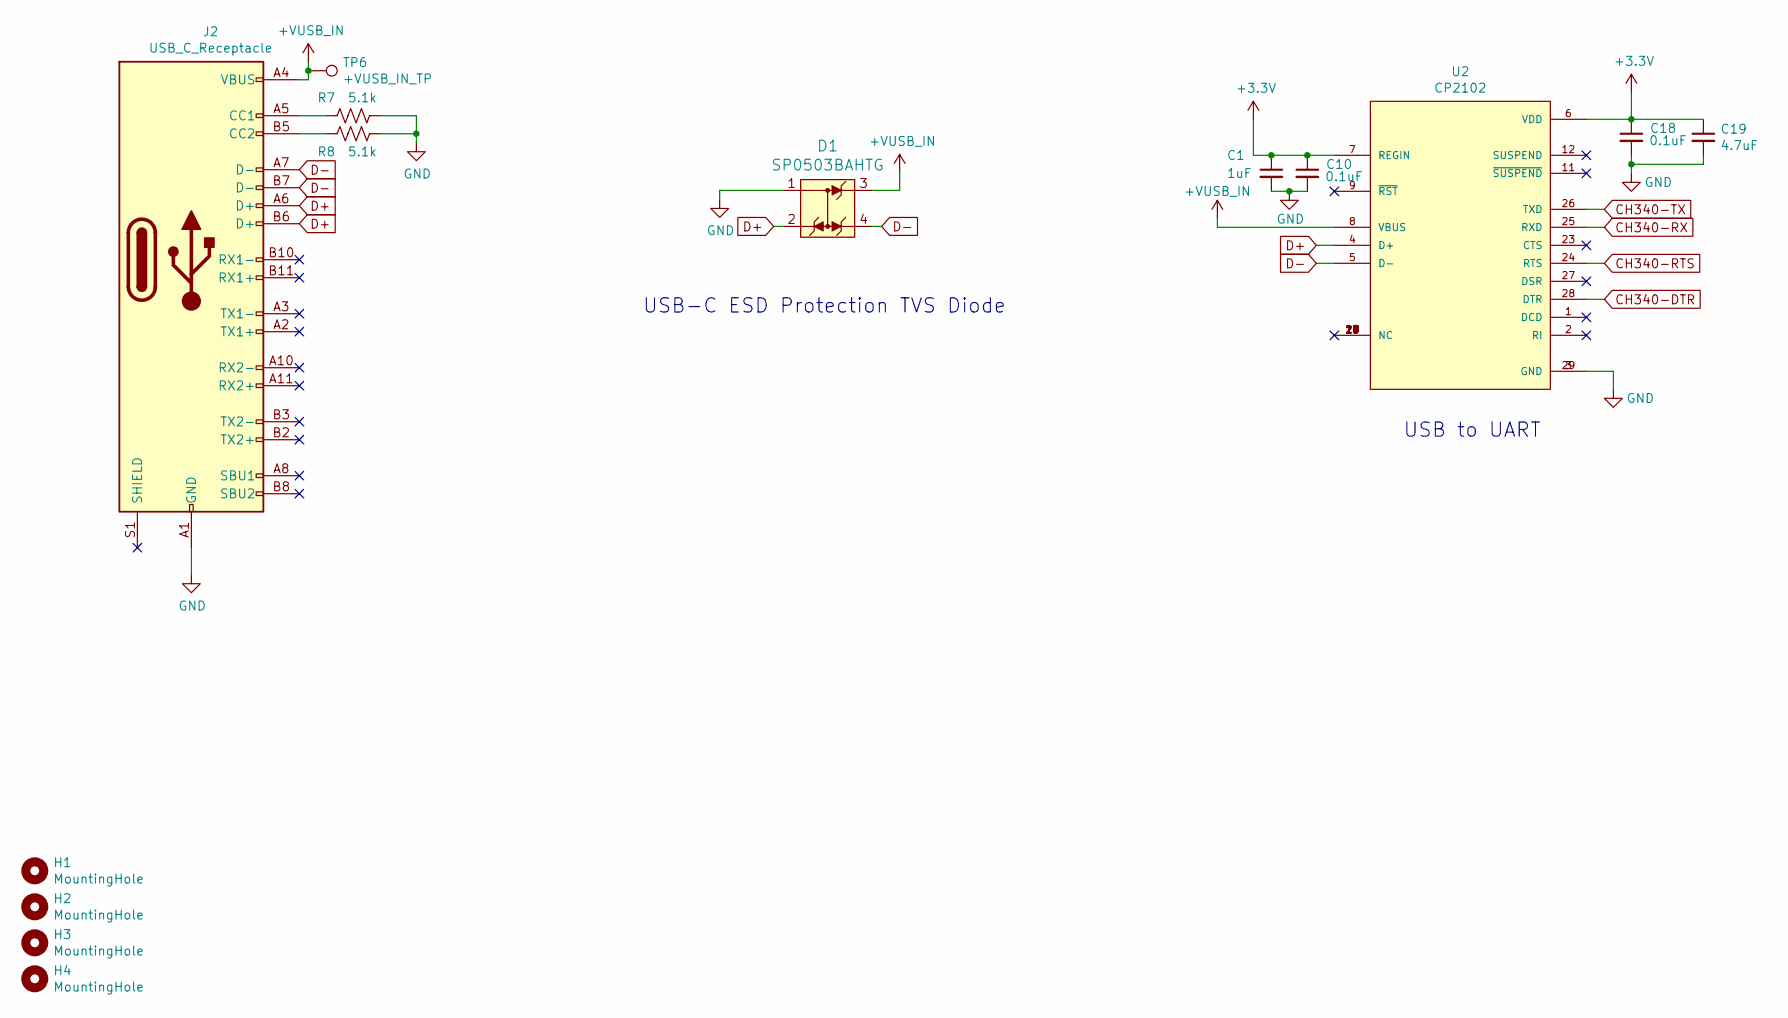
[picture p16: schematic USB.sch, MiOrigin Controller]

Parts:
C1: 1uF; C_0603_1608Metric
C10, C18: 0.1uF; C_0603_1608Metric
C19: 4.7uF; C_0805_2012Metric
D1: SP0503BAHTG; SOT-143-4; MPN SP0503BAHTG; Digi-Key_PN F2715CT-ND
H1, H2, H3, H4: MountingHole; MountingHole_3.2mm_M3_DIN965_Pad_TopBottom
J2: USB_C_Receptacle; USB_C_Receptacle_GCT_USB4085; MPN USB4085-GF-A
R7, R8: 5.1k; R_0603_1608Metric
TP6: +VUSB_IN_TP; TestPoint_Pad_D2.0mm
U2: CP2102; QFN50P500X500X100-29N

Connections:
+3V3: C1.1, C10.1, C18.1, C19.1, U2.6 (VDD), U2.7 (REGIN); also elsewhere on the board
+VUSB_IN: D1.3, J2.A4 (VBUS), J2.A9 (VBUS), J2.B4 (VBUS), J2.B9 (VBUS), TP6.1, U2.8 (VBUS); also elsewhere on the board
CH340-DTR: U2.28 (DTR); also elsewhere on the board
CH340-RTS: U2.24 (RTS); also elsewhere on the board
CH340-RX: U2.25 (RXD); also elsewhere on the board
CH340-TX: U2.26 (TXD); also elsewhere on the board
D+: D1.2, J2.A6 (D+), J2.B6 (D+), U2.4 (D+)
D-: D1.4, J2.A7 (D-), J2.B7 (D-), U2.5 (D-)
GND: C1.2, C10.2, C18.2, C19.2, D1.1, J2.A1 (GND), J2.A12 (GND), J2.B1 (GND), J2.B12 (GND), R7.1, R8.1, U2.3 (GND), U2.29 (GND); also elsewhere on the board
unnamed: J2.A5 (CC1), R7.2
unnamed: J2.B5 (CC2), R8.2
unnamed: U2.10 (NC), U2.13 (NC), U2.14 (NC), U2.15 (NC), U2.16 (NC), U2.17 (NC), U2.18 (NC), U2.19 (NC), U2.20 (NC), U2.21 (NC), U2.22 (NC)

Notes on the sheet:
USB-C ESD Protection TVS Diode
USB to UART

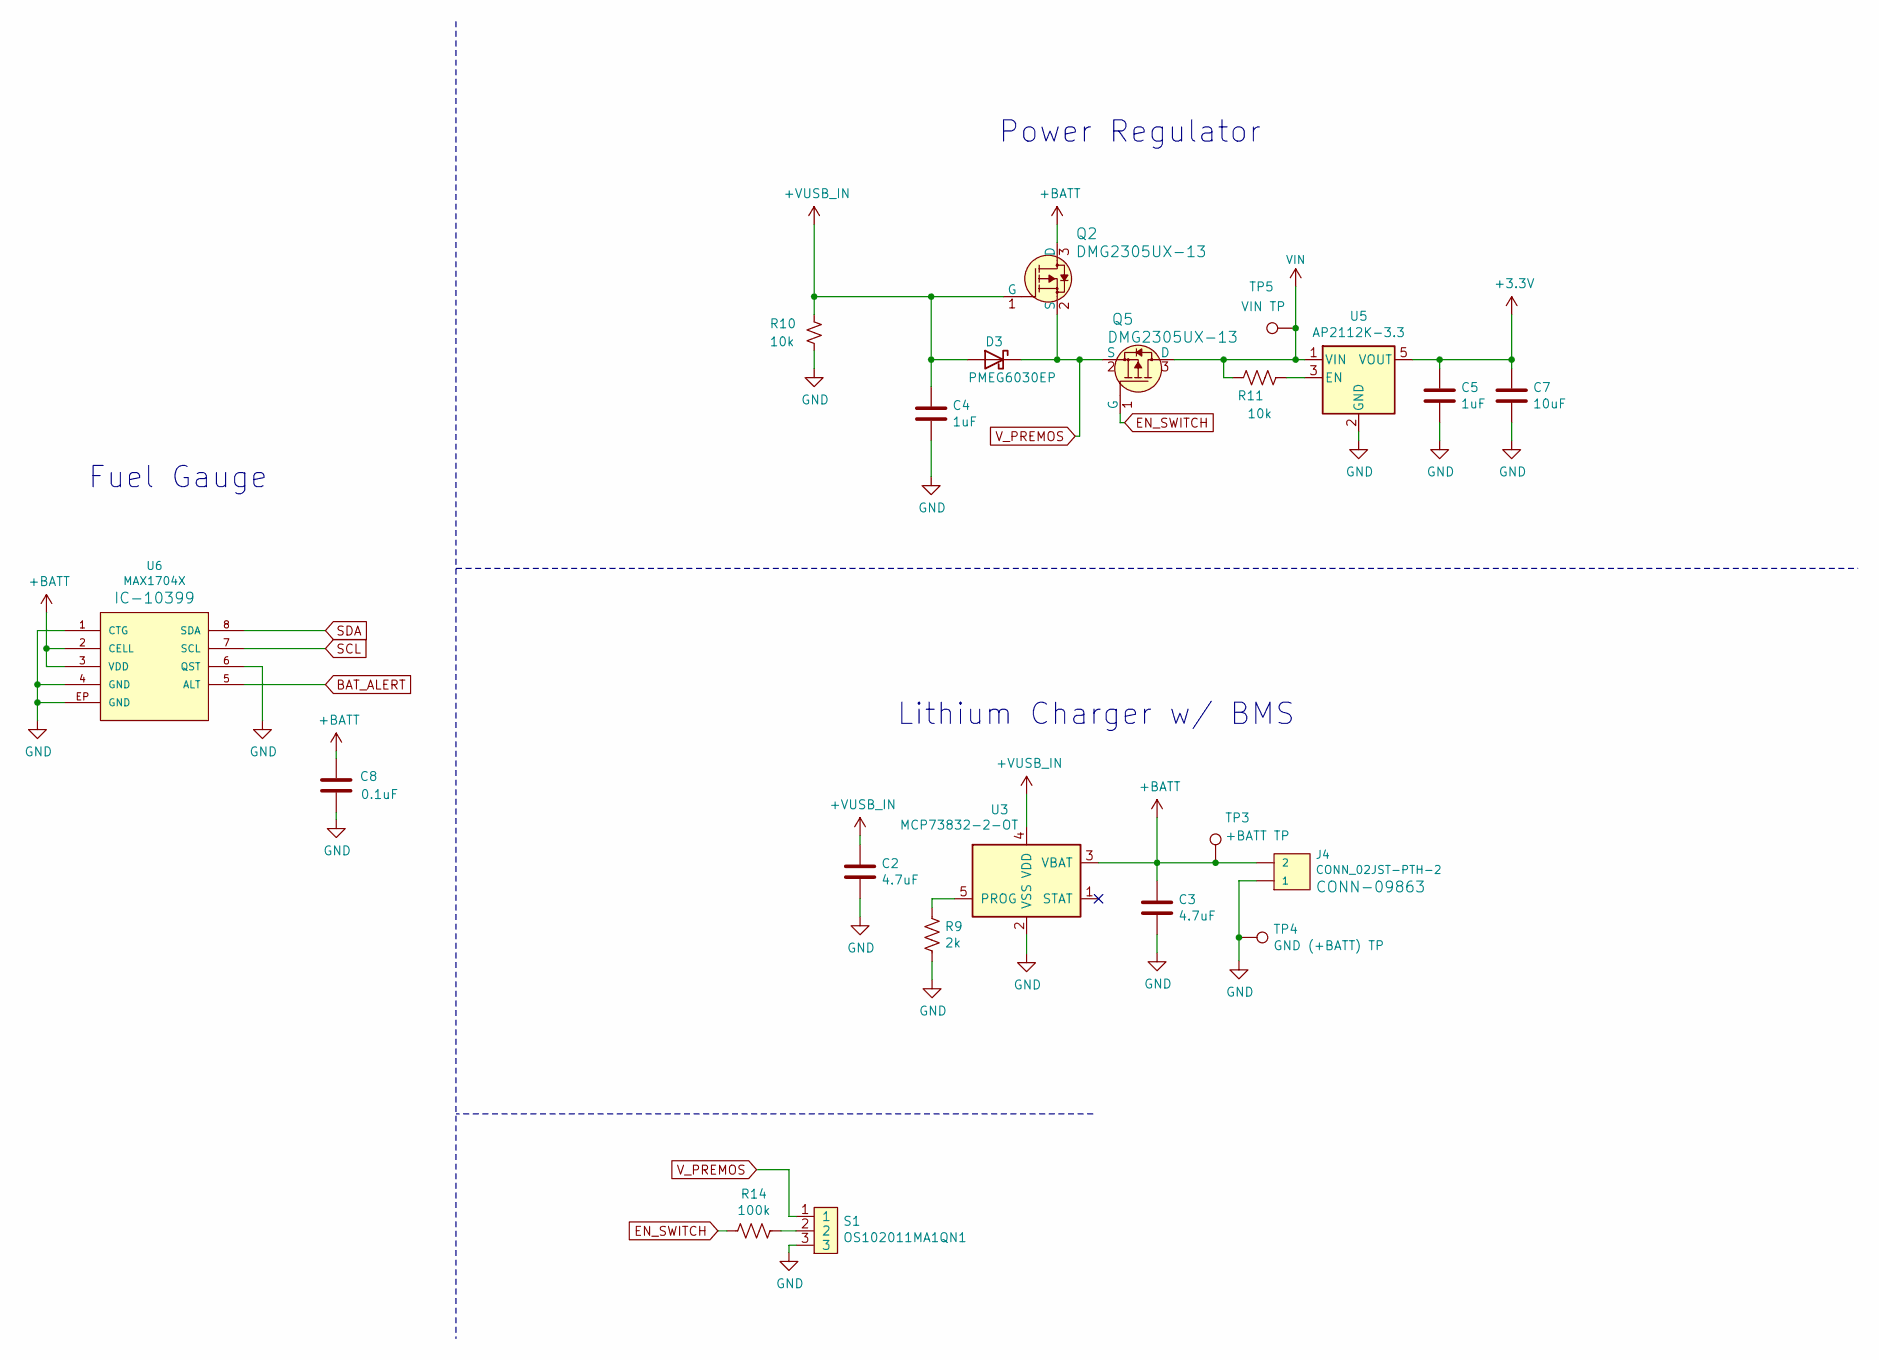
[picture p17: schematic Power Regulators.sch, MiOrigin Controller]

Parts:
C2, C3: 4.7uF; C_0805_2012Metric
C4, C5: 1uF; C_0603_1608Metric
C7: 10uF; C_1206_3216Metric
C8: 0.1uF; C_0603_1608Metric
D3: PMEG6030EP; D_SOD-128; MPN PMEG6030EP,115
J4: CONN_02JST-PTH-2; JST-2-PTH
Q2, Q5: DMG2305UX-13; SOT-23-3; MPN DMG2305UX-13; Digi-Key_PN DMG2305UX-13DICT-ND
R9: 2k; R_0603_1608Metric
R10, R11: 10k; R_0603_1608Metric
R14: 100k; R_0603_1608Metric
S1: OS102011MA1QN1
TP3: +BATT TP; TestPoint_Pad_D2.0mm
TP4: GND (+BATT) TP; TestPoint_Pad_D2.0mm
TP5: VIN TP; TestPoint_Pad_D2.0mm
U3: MCP73832-2-OT; SOT-23-5
U5: AP2112K-3.3; SOT-23-5
U6: MAX1704X; SON50P200X200X80-9N; MPN MAX17048G+T10

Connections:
+3V3: C5.1, C7.1, U5.5 (VOUT); also elsewhere on the board
+BATT: C3.1, C8.2, J4.2, Q2.3 (D), TP3.1, U3.3 (VBAT), U6.2 (CELL), U6.3 (VDD)
+VUSB_IN: C2.1, C4.1, D3.2 (A), Q2.1 (G), R10.1, U3.4 (VDD); also elsewhere on the board
BAT_ALERT: U6.5 (ALT); also elsewhere on the board
EN_SWITCH: Q5.1 (G), R14.2
GND: C2.2, C3.2, C4.2, C5.2, C7.2, C8.1, J4.1, R9.2, R10.2, S1.3, TP4.1, U3.2 (VSS), U5.2 (GND), U6.1 (CTG), U6.4 (GND), U6.6 (QST), U6.EP (GND); also elsewhere on the board
unnamed: R9.1, U3.5 (PROG)
unnamed: R11.1, U5.3 (EN)
unnamed: R14.1, S1.2
SCL: U6.7 (SCL); also elsewhere on the board
SDA: U6.8 (SDA); also elsewhere on the board
VIN: Q5.3 (D), R11.2, TP5.1, U5.1 (VIN)
V_PREMOS: D3.1 (K), Q2.2 (S), Q5.2 (S), S1.1

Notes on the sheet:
Power Regulator
Fuel Gauge
Lithium Charger w/ BMS

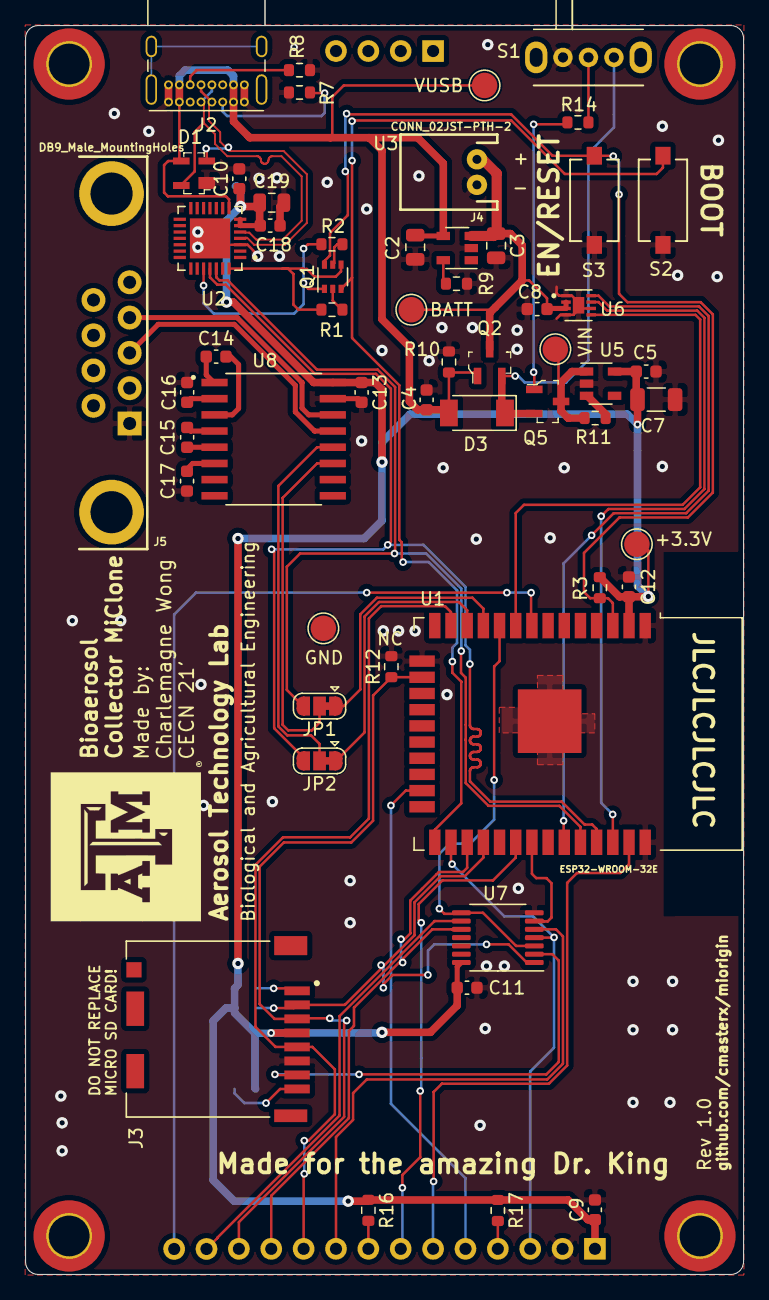
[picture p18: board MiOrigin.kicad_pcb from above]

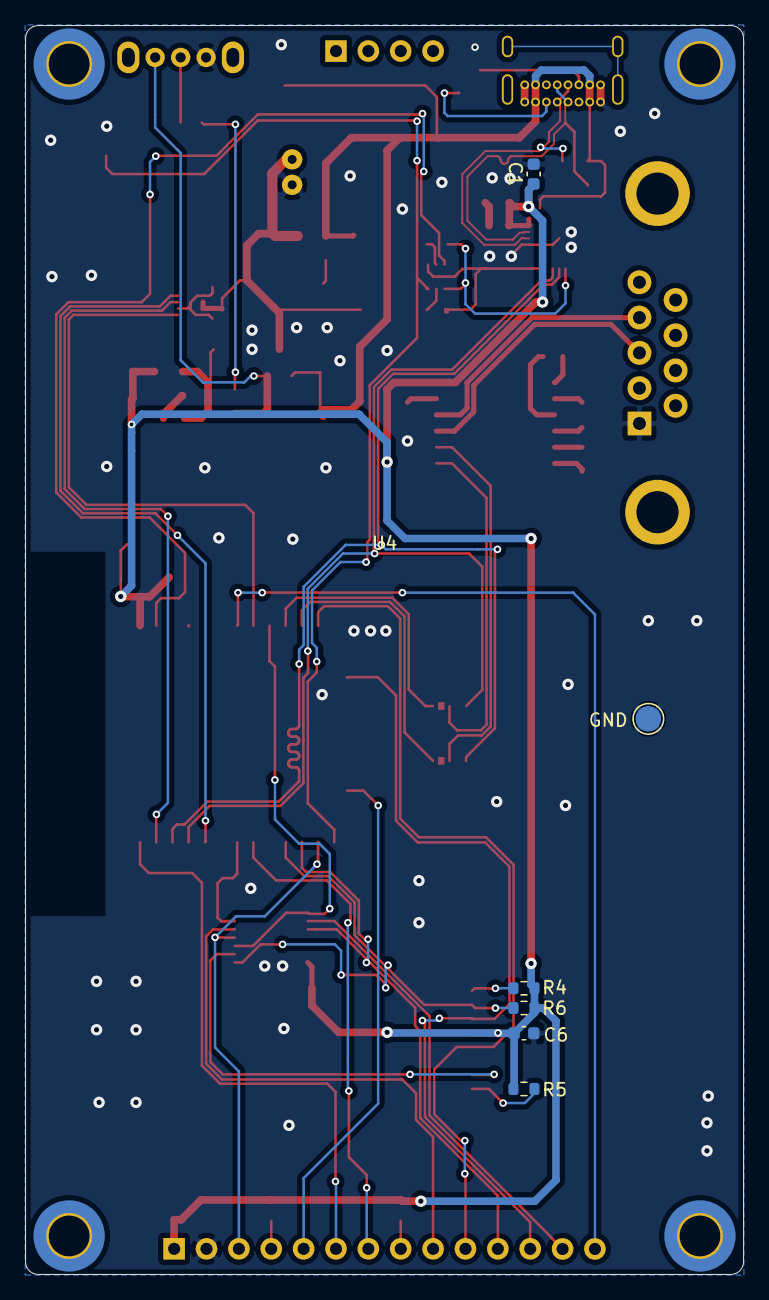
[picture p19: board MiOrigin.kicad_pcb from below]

Board: 2 copper layers, 56.3 x 98.0 mm, 66 parts (7 on the bottom side), 56 nets.

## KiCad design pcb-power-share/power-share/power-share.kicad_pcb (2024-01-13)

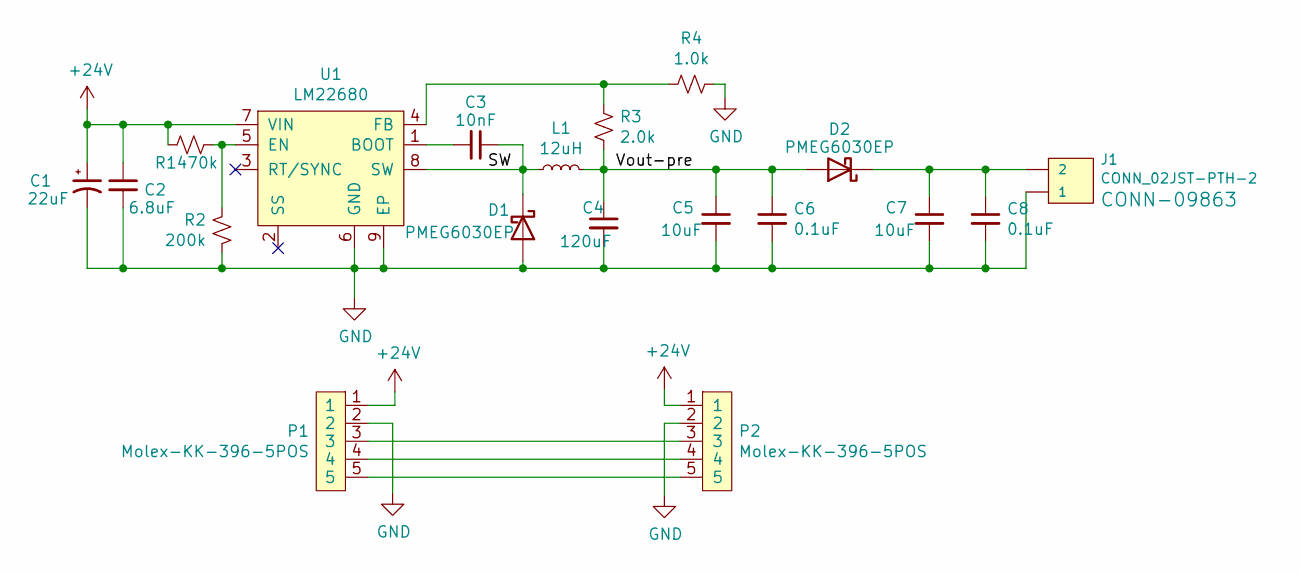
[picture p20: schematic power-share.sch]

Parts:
C1: 22uF; CP_Elec_8x6.5
C2: 6.8uF; C_1812_4532Metric
C3: 10nF; C_0402_1005Metric_Pad0.74x0.62mm_HandSolder
C4: 120uF; C_Elec_4x5.8
C5, C7: 10uF; C_0805_2012Metric
C6, C8: 0.1uF; C_0603_1608Metric
D1, D2: PMEG6030EP; D_SOD-128
J1: CONN_02JST-PTH-2; JST-2-PTH
L1: 12uH; L_Bourns_SRR1260
P1, P2: Molex-KK-396-5POS
R1: 470k; R_0603_1608Metric
R2: 200k; R_0603_1608Metric
R3: 2.0k; R_0603_1608Metric
R4: 1.0k; R_0603_1608Metric
U1: LM22680

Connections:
+24V: C1.1, C2.1, P1.1, P2.1, R1.1, U1.7 (VIN)
/SW: C3.1, D1.1 (K), L1.1, U1.8 (SW)
/Vout-pre: C4.1, C5.1, C6.1, D2.2 (A), L1.2, R3.2
GND: C1.2, C2.2, C4.2, C5.2, C6.2, C7.2, C8.2, D1.2 (A), J1.1, P1.2, P2.2, R2.1, R4.1, U1.6 (GND), U1.9 (EP)
unnamed: C3.2, U1.1 (BOOT)
unnamed: C7.1, C8.1, D2.1 (K), J1.2
unnamed: P1.3, P2.3
unnamed: P1.4, P2.4
unnamed: P1.5, P2.5
unnamed: R1.2, R2.2, U1.5 (EN)
unnamed: R3.1, R4.2, U1.4 (FB)

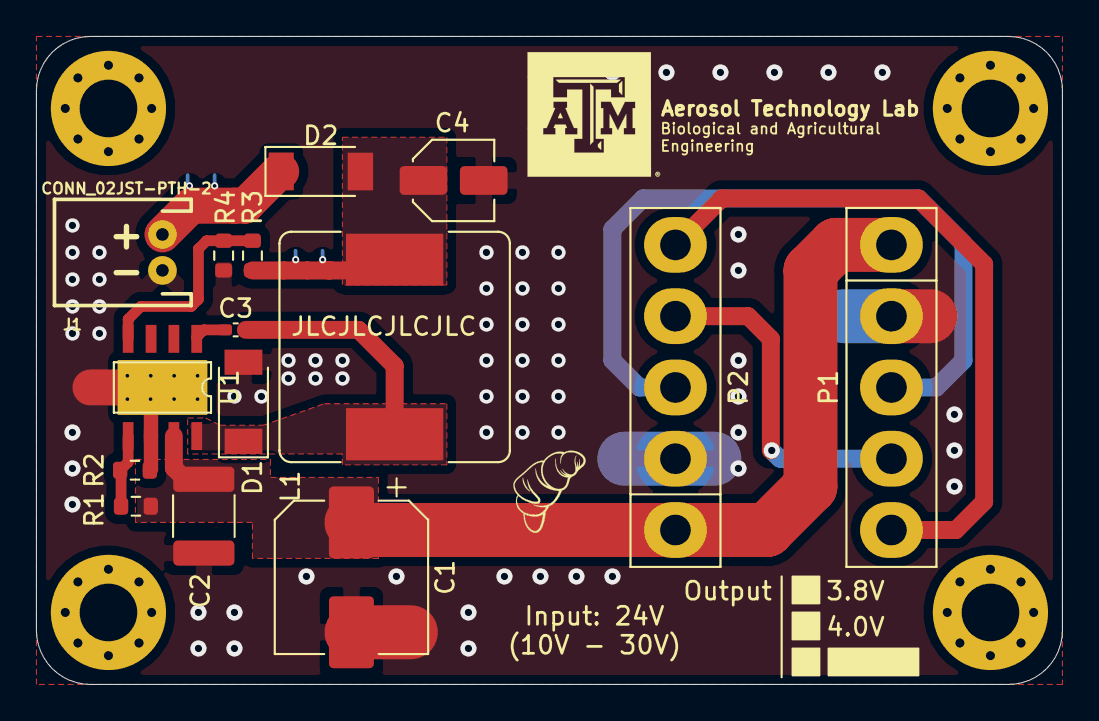
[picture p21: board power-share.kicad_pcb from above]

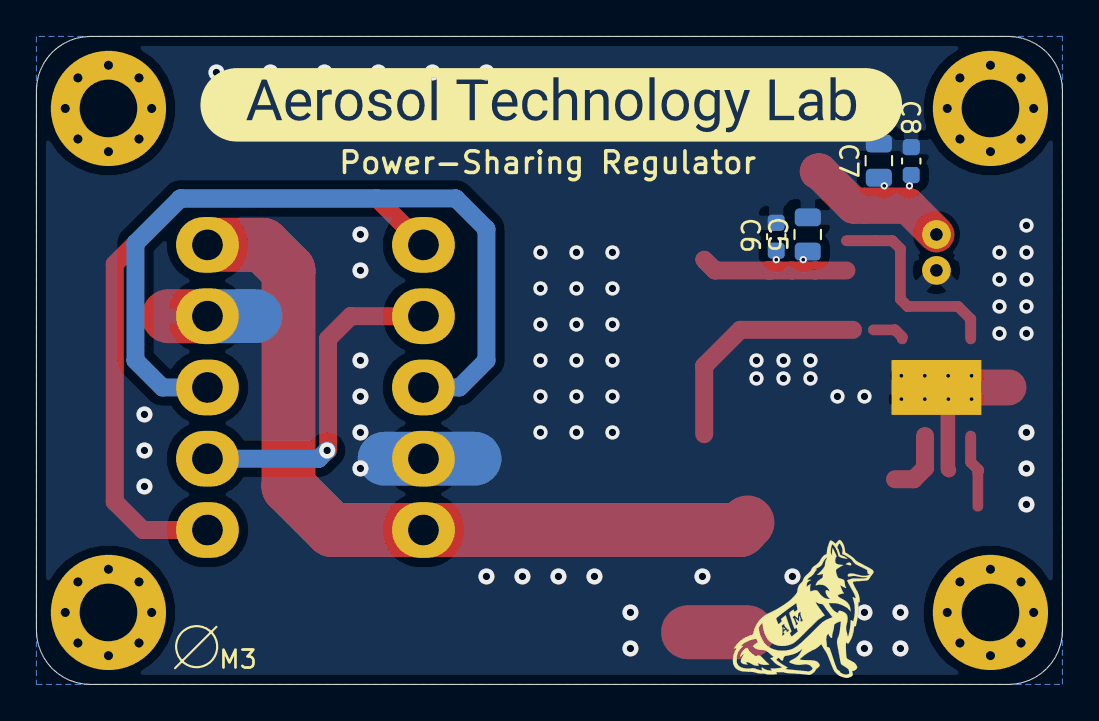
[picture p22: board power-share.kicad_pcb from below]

Board: 2 copper layers, 57.0 x 36.0 mm, 20 parts (5 on the bottom side), 11 nets.

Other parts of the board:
kibuzzard-61710895: G***; label

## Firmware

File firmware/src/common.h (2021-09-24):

// common properties shared by factory and ota firmware

#pragma once

#define RS232_RX2 27
#define RS232_TX2 26

#define I2C_SDA 21
#define I2C_SCL 22

#define VSPI_MISO MISO
#define VSPI_MOSI MOSI
#define VSPI_SCLK SCK
#define VSPI_SS 4

#define HSPI_MISO 25
#define HSPI_MOSI 13
#define HSPI_SCLK 14
#define HSPI_SS 17

#define SD_CS 17
#define LCD_CS 4
#define TCH_CS 16

#define LCD_DC 15

#define TCH_INT 32

#define LINE_TERMINATION    (uint16_t) 0x0D0A
#define FLUSH_SERIAL        (uint16_t) 0x0000

#include <Arduino.h>
#include <SPI.h>

extern SPIClass *vspi;
extern SPIClass *hspi;

void hardReset();

void Common_Init();

/**
 * @brief 
 * 
 * @param buffer 
 * @parstrcmpam stream 
 */
size_t readUntilEnd(char *buffer, size_t bufferSize, Stream &stream);

void Common_USBC_Handler(void *params);

void Common_HEX_print(char *cstr, Stream &stream = Serial);

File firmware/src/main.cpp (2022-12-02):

// if true, compile factory firmware instead

#ifdef FACTORY

// these are defined in factory.cpp
extern void setup();
extern void loop();

#else

#include "config.h"
#include <Arduino.h>
// #include "credentials.h"
#include "common.h"
#include <memory>
#include <FS.h>
#include <SPI.h>
#include <SPIFFS.h>
#include <SD.h>
#include <esp_ota_ops.h>
#include <esp_task_wdt.h>
#include <BLE2902.h>
#ifdef WIFI_CONNECTIVITY_ENABLE
    #include <WiFi.h>
    #include <HTTPClient.h>
    #include "wifisys/WiFiController.h"
    #include "wifisys/WiFi_WPA_Connection.h"
    #include "WiFiOTAUpdater.h"
#endif
#include <BLEDevice.h>
#include <BLEUtils.h>
#include <BLEServer.h>
#include <ArduinoJson.h>
#include <TFT_eSPI.h>
#include "driver/tftdisplay.h"
#include "driver/touchscreen.h"
#include "driver/lipo.h"
#include "driver/miclone.hpp"
#include "MutexRAII.hpp"
#include "BLE_Callback_Coms.h"
#include "BLE_UUID.h"
#include "utils.h"
#include "DisplaySetup.h"       // this line must be after including TFT_eSPI.h
#include "rom/md5_hash.h"
#include <hwcrypto/aes.h>
#include <mbedtls/rsa.h>
#include <string>

// pages
#include "graphics/Graphics.hpp"
#include "pages/AppPageConfig.hpp"
#include "pagesystem/pagesystem.h"
#include "pagesystem/pageoptions.h"
#include "pages/Calibration.h"
#include "pages/Debug.hpp"
#include "pages/Home.hpp"

// tests
#include "test/post_setup.hpp"

// extract arduino core props
#if CONFIG_FREERTOS_UNICORE
#define ARDUINO_RUNNING_CORE 0
#else
#define ARDUINO_RUNNING_CORE 1
#endif

#define MAJOR_FIRMWARE_VERSION 0
#define MINOR_FIRMWAR_VERSION  6

QueueHandle_t tsQueue;

TaskHandle_t usbcHandler = nullptr;

BLE_Callback_Coms callbackComs;

PageSystem_t devicePageManager;

SemaphoreHandle_t graphicsMutex;

using Driver::tft;

using Driver::ts;

/**
 * @brief Struct containing device info. Contents
 *        will be populated during setup
 * 
 */
struct {
    char deviceName[17] = "NONE";
    uint16_t id = (uint16_t) 0xFFFF;
    char pcbRev[17] = "NULL";
    char uuid[40] = "";
} DevinceInfo;

#ifdef ENABLE_BLE
struct {

    BLEServer *pServer;

    struct {

        BLEService *pService;
        BLECharacteristic *pDeviceName;
        BLECharacteristic *pComs;
        
    } device;
    
    /**
     * @brief Puts BLE modem to sleep
     * 
     */
    void sleep()
    {
        if (pServer) {
            pServer->getAdvertising()->stop();
            ESP_ERROR_CHECK(esp_bt_sleep_enable());
        }
    }

    /**
     * @brief Wakes up BLE modem
     * 
     */
    void wakeup()
    {
        if (pServer) {
            ESP_ERROR_CHECK(esp_bt_sleep_disable());
            pServer->getAdvertising()->start();
        }
    }

    
} BLE_Props;
#endif

/**
 * @brief Parses command from a given string that starts with an exclamation mark
 * 
 * @param buffer 
 * @param buffer_length 
 * @param command 
 * @param command_length 
 * @return size_t 
 */
size_t parseCommandFromString(const char *buffer, size_t buffer_length, char *command, size_t command_length)
{
    if (buffer_length && buffer[0] == '!') {
        size_t i;
        for (i = 1; i < buffer_length && i < command_length && (buffer[i] != '\0' || buffer[i] != '\r' || buffer[i] != ' '); ++i) {
            command[i - 1] = buffer[i];
        }

        return i;
    }

    return 0;
}

/**
 * @brief Handles responses to UART from USB-C
 * 
 * @param parameters 
 */
void handleUSBC(void *parameters = nullptr)
{
    const TickType_t waitDelay = 1000 / portTICK_PERIOD_MS;

    delay(200);
    Serial.flush();
    delay(200);
    
    while (true) {
        
        if (Serial.available()) {
            String message = Serial.readString();
            
            #ifdef DEV_DEBUG
            {
                Serial.print("\nDebug hex raw: ");
                Serial.printf("\nDebug hex raw: %s\n", message.c_str());
                for(const char c : message) {
                    Serial.printf("%02X ", c);
                }
            }
            #endif
            
            size_t messageLen = message.length();

            if (messageLen && messageLen < 256) {
                // can perform string checks

                
                if (message[0] == '/') {
                    // this is a command from MiClone
                    
                    // bypass mode
                    Serial2.write(reinterpret_cast<const uint8_t *>(message.c_str()), message.length());
                    
                    File miCloneEmulationLog = SD.open(MICLONE_LOG_FILENAME, "w+");
                    if (miCloneEmulationLog) {
                        
                        Serial.printf("File is valid, printing \"%s\"", message.c_str());
                        const char printBuffer[] = "-> ";
                        miCloneEmulationLog.seek(miCloneEmulationLog.size());
                        miCloneEmulationLog.write(reinterpret_cast<const uint8_t *>(printBuffer), strlen(printBuffer));
                        miCloneEmulationLog.write(reinterpret_cast<const uint8_t *>(message.c_str()), message.length());
                    }

                    miCloneEmulationLog.close();
                    delay(10);
                }
                else if (message[0] == '!') {
                    // command from my helper program
                    // todo
                    char command[17] = { 0 };
                    size_t offset = 0;
                    offset = parseCommandFromString(message.c_str(), message.length(), command, sizeof(command));

                    // Serial.print("  Result of command: ");
                    // Serial.println(command);
                    // Serial.print("  Result of strcmp(command, \"ping\"): ");
                    // Serial.println(!strcmp(command, "ping"), DEC);

                    if (!strcmp(command, "sd") || !strcmp(command, "spiffs")) {

                        // FS &fs = !strcmp(command, "!sd") ? *(dynamic_cast<fs::FS *>)(&SD) : *(dynamic_cast<fs::FS *>)(&SPIFFS);
                        
                        offset = nextSubString(message.c_str(), offset, message.length(), command, sizeof(command));
                        bool commandError = false;      // true when there is an invalid input to the command
                        
                        if (offset) {
                            if (!strcmp(command, "read")) {
                                // File f = SD.open()
                                
                            }
                            else if (!strcmp(command, "write")) {

                            }
                            else {
                                commandError = true;
                            }
                        }
                        else {
                            commandError = true;
                        }

                        utilsPrint("~Invalid '!file' command. Options are: ~file [write | read] [filename] ");
                    }
                    else if (!strcmp(command, "ping")) {
                        Serial.println("pong!");
                    }
                    else if (!strcmp(command, "boot-factory")) {
                        const esp_partition_t *currentParition = esp_ota_get_running_partition();
                        const esp_partition_t *factoryPartition = esp_partition_find_first(ESP_PARTITION_TYPE_APP, ESP_PARTITION_SUBTYPE_APP_FACTORY, nullptr);
                        ESP_ERROR_CHECK(esp_ota_set_boot_partition(factoryPartition));

                        const esp_partition_t *newBootParition = esp_ota_get_boot_partition();

                        if (newBootParition == factoryPartition) {
                            Serial.print("Booting to factory partition in");
                            for (int i = 3; i > 0; --i) {
                                Serial.print(i);
                                Serial.print(" ...");
                                Serial.println("This does not work. Maybe that to trigget ESP.restart() correctly, we have to restart immediately after partition select or use CPU1 to perform the reset");
                                assert(false);
                                delay(1000);
                            }

                            ESP.restart();
                        }
                        else if (newBootParition == currentParition) {
                            Serial.println("Error: Failed to select factory partition. Next boot will be current partition");
                        }
                        else {
                            Serial.println("Error: Partition is booting to something else! It is neither factory or firmware (ota0)");
                        }
                    }
                    else if (!strcmp(command, "touchscreen")) {
                        assert(false && "This command is not working.");    // possible causes is a bug in the nextSubstring function
                        dev_println("=> Processing touchscreen command...");
                        offset = nextSubString(message.c_str(), offset, message.length(), command, sizeof(command));
                        if (!offset) continue;
                        if (strcmp(command, "rotate")) continue;        // this is in a separate if statement for future reference

                        dev_println("=> Processing rotation sub command...");
                        offset = nextSubString(message.c_str(), offset, message.length(), command, sizeof(command));
                        if (!offset) continue;

                        if (command[0] >= '0' && command[0] < '9') {
                            int rotation = atoi(command);
                            Driver::ts.setRotation(rotation);
                            Serial.printf("-> Rotation set to %d\n", rotation % 4);
                        }
                        else {
                            Serial.println("-> Cannot process request because the arguments passed is invalid");
                        }
                    }
                    else if (!strcmp(command, "device-name")) {
                        Serial.print("-> Device Name: ");
                        Serial.println(DevinceInfo.deviceName);
                    }
                    else if (!strcmp(command, "device-raw")) {
                        if (SPIFFS.exists("/device_info")) {
                            File f = SPIFFS.open("/device_info", "r");

                            char sendBuffer[256] = { 0 };
                            sprintf(sendBuffer, "name %s size %08X", f.name(), f.size());
                            Serial.print(sendBuffer);
                            Serial.write(f);
                            f.close();
                        }
                        else {
                            Serial.println("Error: Cannot find device info file. Flash new filesystem image");
                        }
                    }
                    else if (!strcmp(command, "stop")) {
                        Driver::miclone_stop();
                    }
                    else if (!strcmp(command, "help")) {
                        
                        if (!SPIFFS.exists("/help.txt")) {
                            Serial.println("Error: Cannot find \"help.txt\" in SPIFFS");
                            continue;
                        }

                        File f = SPIFFS.open("/help.txt");
                        if (f.isDirectory()) {
                            Serial.println("Error: \"help.txt\" is a directory and not a file");
                            f.close();
                            continue;
                        }

                        Serial.println(f);
                        f.close();
                    }
                }
                else if (message[0] == '$') {

                    char msgCpy[64];
                    strncpy(msgCpy, message.c_str(), sizeof(msgCpy) - 1);
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

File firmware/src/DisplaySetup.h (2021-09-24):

//                            USER DEFINED SETTINGS
//   Set driver type, fonts to be loaded, pins used and SPI control method etc
//
//   See the User_Setup_Select.h file if you wish to be able to define multiple
//   setups and then easily select which setup file is used by the compiler.
//
//   If this file is edited correctly then all the library example sketches should
//   run without the need to make any more changes for a particular hardware setup!
//   Note that some sketches are designed for a particular TFT pixel width/height


// ##################################################################################
//
// Section 1. Call up the right driver file and any options for it
//
// ##################################################################################

// Define STM32 to invoke optimised processor support (only for STM32)
//#define STM32

// Defining the STM32 board allows the library to optimise the performance
// for UNO compatible "MCUfriend" style shields
//#define NUCLEO_64_TFT
//#define NUCLEO_144_TFT

// STM32 8 bit parallel only:
// If STN32 Port A or B pins 0-7 are used for 8 bit parallel data bus bits 0-7
// then this will improve rendering performance by a factor of ~8x
//#define STM_PORTA_DATA_BUS
//#define STM_PORTB_DATA_BUS

// Tell the library to use 8 bit parallel mode (otherwise SPI is assumed)
//#define TFT_PARALLEL_8_BIT

// Display type -  only define if RPi display
//#define RPI_DISPLAY_TYPE // 20MHz maximum SPI
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

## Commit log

2021-06-24 Initial push
    [MiOrigin-B_Cu.gbl, MiOrigin-B_Mask.gbs, MiOrigin-B_Paste.gbp, MiOrigin-B_SilkS.gbo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]
2021-06-25 Replace USB to UART with CP2102-GM
    [MiOrigin.kicad_pcb, MiOrigin.sch, Power Regulators.sch, USB.sch]
2021-07-01 Update board
    [MiOrigin-B_Cu.gbl, MiOrigin-B_Mask.gbs, MiOrigin-B_Paste.gbp, MiOrigin-B_SilkS.gbo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]
2021-07-01 Move pcb files to its own folder
    [MiOrigin-B_Cu.gbl, MiOrigin-B_Mask.gbs, MiOrigin-B_Paste.gbp, MiOrigin-B_SilkS.gbo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]
2021-07-03 Update board info
    [partition_table.csv]
2021-07-14 Update partition table
    [partition_table.csv]
2021-07-17 Add data information about each device. Untested
2021-07-27 Add new property to device info and cleanup code handling aquisition of device info
2021-07-27 Fix print on touch screen data
2021-07-27 Add battery - MAX178048 driver
2021-07-31 Add WiFi manager to manage several WiFi connections, keep WiFi alive, and WiFi power savings
2021-08-03 Prettied up prints on serial and display
2021-08-05 Few updates
    [MiOrigin.sch, Power Regulators.sch, USB.sch]
2021-08-15 Update board information to reflect useable RAM in ESP32-WROOM-32E (16MB)
2021-08-15 Add dev macro for prints
2021-08-15 Update factory firmware to reflect new method of debug prints
2021-08-15 Fix file not closed when reading device information
2021-08-16 Working calibration screen
2021-08-16 Fix calibration bug on the y-axis
2021-08-31 Misc changes - add calibration button
2021-09-22 Add testing framework
2021-09-28 Fix bug due to hardware issue in controller. The capacitors near the MAX3232 cannot hold its rated capacitance when it is charged near 15V (the IC charges the capacitors to 12V)
2022-01-11 Add compile flag (enabled via config.h) to enable sample waste toggle flag. This should be disabled
2022-01-11 Change print in stop signal to only display when dev debug mode is enabled
2023-08-12 Add pcb powershare pcb
    [LM22680.step, kk396-5pos.stp, power-share-B_Cu.gbl, power-share-B_Mask.gbs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]
